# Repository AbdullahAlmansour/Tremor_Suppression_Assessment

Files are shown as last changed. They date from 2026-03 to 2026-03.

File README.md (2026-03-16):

# Tremor Suppression Assessment
This repository includes the instructions to build simple and affordable devices to test wrist exoskeletons for tremor suppression, which includes:
1 - a three-point bending machine to measure the stiffness,
2 - and an oscillatory wrist joint to simulate wrist tremor.
## 1 - Three Point Bending Device
This device was designs to assess the stiffness of a small exoskeleton. A linear displacement is applied on the exoskeleton by means of a servo motor and rack-and-pinion gearbox, and a load-cell is attached to the end effector to measure the applied force. 

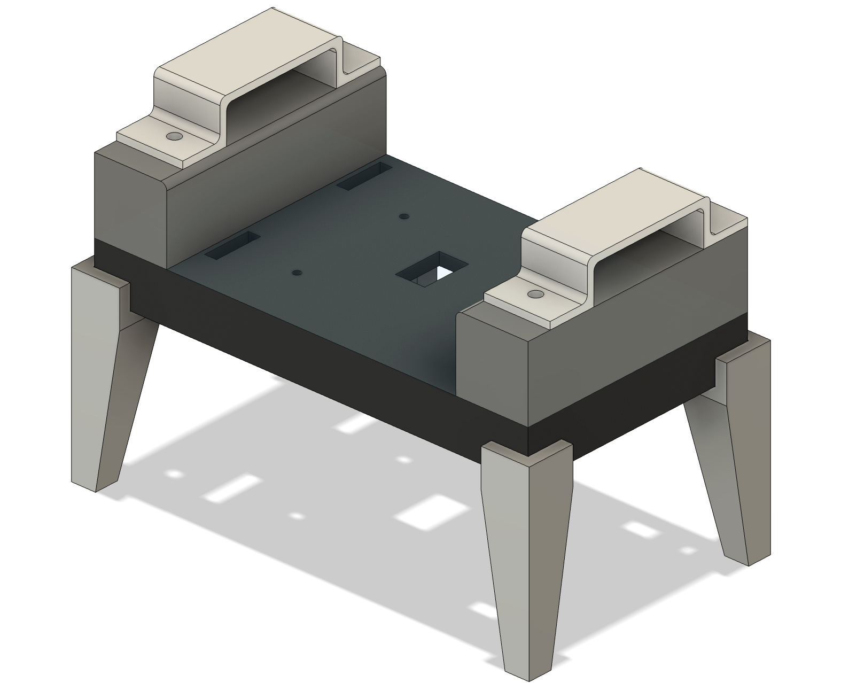
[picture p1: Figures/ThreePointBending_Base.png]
Base setup
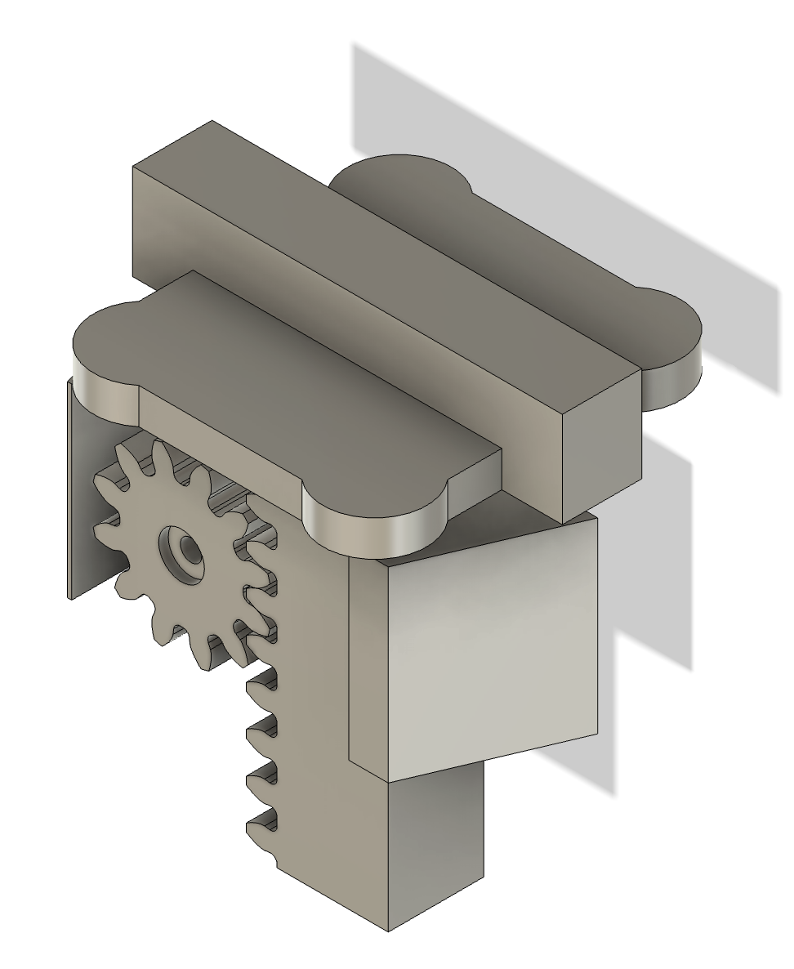
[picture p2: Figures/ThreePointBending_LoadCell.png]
Load cell setup
|  |  |
| :-----------------------------------------------: | :--------------------------------------------------------: |
|             **Figure 1:** Base setup              |               **Figure 2:** Load cell setup                |

The device consists of two main components:
- a base (Figure 1)
- an end effector (Figure 2)

The base was designed to securely hold the sample during testing and to mount the servo motor in the appropriate position. Its modular design allows stiffness measurements at different points of the exoskeleton. The end effector is actuated by an MG996R servo motor, where its angular displacement is converted into a linear displacement by means of a spur-to-linear gearbox. The tip of the end effector distributes the applied force equally onto four load cells encapsulated in a 3D-printed cap. These load cells are arranged in a Wheatstone bridge configuration, enabling precise measurement of small resistance changes, which are caused by mechanical deformation under load. 

The Wheatstone bridge converts resistance variations into a differential voltage signal in the millivolt range. To process this signal, the HX711 analog-to-digital converter (ADC) was used to amplify, filter, and digitise the output. The HX711 is a precision 24-bit ADC that is widely used in weighing scales and industrial control, designed specifically to interface with Wheatstone bridge sensors. It communicates with microcontrollers using a custom two-wire serial protocol (DT and SCK), accessible via the HX711\_ADC library. The HX711 continuously samples the signal and holds the converted data until clocked by the microcontroller, operating at a rate of $10~\mathrm{Hz}$.

### Tools and Components
- FDM 3D Printer (Flashforge 5M Adventurer was used)
- Caliber
- [MG996R Servo Motor](https://www.amazon.co.uk/Pzsmocn-Degrees-Helicopters-Robotic-Various/dp/B0CLGWKP3L/ref=sr_1_7?crid=2HTHPGAJ56Y6U&dib=eyJ2IjoiMSJ9.wogc4i2BFmTbbp_1KzUuA4kjO1IvbSnwEaeE4fUBs91m2Kxkljl7Gbayk552s1KByzJUdnbsghUo5_gd1sdZrULkUjtG6UXABx_IxFpicO-uQWcX5_VTm32dgz2BkLXvxuA14cW1wh0_4t-dmxXxa7OfmbNNnjPDXTDJ-t9xG873xbnqu7wY6JP6vZUN2P8INuiDiu57QHEsjP021zp0o9H9o6Igb4kDpZX3XIvhaG3LGmFQNnW7mmIch3pHO8D3ZLJ-1a-PGwNV_9ktzsRNQ9uoW8n37bhnylQkFCU67k8.gYzW6-Sh9fmm2UNK9i2hZv0QaoHroCeRyJPWE6vCacc&dib_tag=se&keywords=MG996R+Servo+Motor&qid=1773281587&sprefix=mg996r+servo+motor%2Caps%2C275&sr=8-7)
- [Four Strain-Gauge Sensors and HX711 Module](https://www.amazon.co.uk/YOUMILE-110lbs-Half-bridge-Weight-Resistance/dp/B07TWLP3X8)  

### Force Calibration

The HX711 ADC returns a unitless raw value $r$ that is proportional to the applied force $F$. Therefore, to determine the linear mapping parameters between the HX711 measurements and the applied force, a set of calibration masses in the range of $m \in [10,500]g$ were used. Assuming a gravitational acceleration of $g = 9.81~\mathrm{m/s^2}$, these masses correspond to an applied force of $F \in [0.0981,4.905] N$. The linear mapping is achieved by determining the parameters in linear equation
$$F = a + b \cdot r$$
where $F$ is the applied force in newtons, $r$ is the unit-less output from the HX711, and $a$, $b$ are the regression coefficients determined from the calibration data.

Given the calibration data vectors for applied force $\mathbf{F} = [F_1, F_2, \ldots, F_n]$ and corresponding raw sensor readings $\mathbf{r} = [r_1, r_2, \ldots, r_n]$, the linear model coefficient $\{a,b\}$ can be found using least squares method

$$
\boldsymbol{\theta} =
\begin{bmatrix}
a \\
b
\end{bmatrix}
= (\mathbf{X}^\top \mathbf{X})^{-1} \mathbf{X}^\top \mathbf{F},
\qquad
\mathbf{X} =
\begin{bmatrix}
1 & r_1 \\
1 & r_2 \\
\vdots & \vdots \\
1 & r_n
\end{bmatrix},
\qquad
\mathbf{F} =
\begin{bmatrix}
F_1 \\
F_2 \\
\vdots \\
F_n
\end{bmatrix}.
$$

where $\mathbf{X}$ is the $n \times 2$ matrix with a column of ones and a column of $r$ values, and $\mathbf{F}$ is the $n \times 1$ vector of measured forces. 

The calibration parameters $a$ and $b$ were found and used to fit the linear line, as shown in Figure 3.

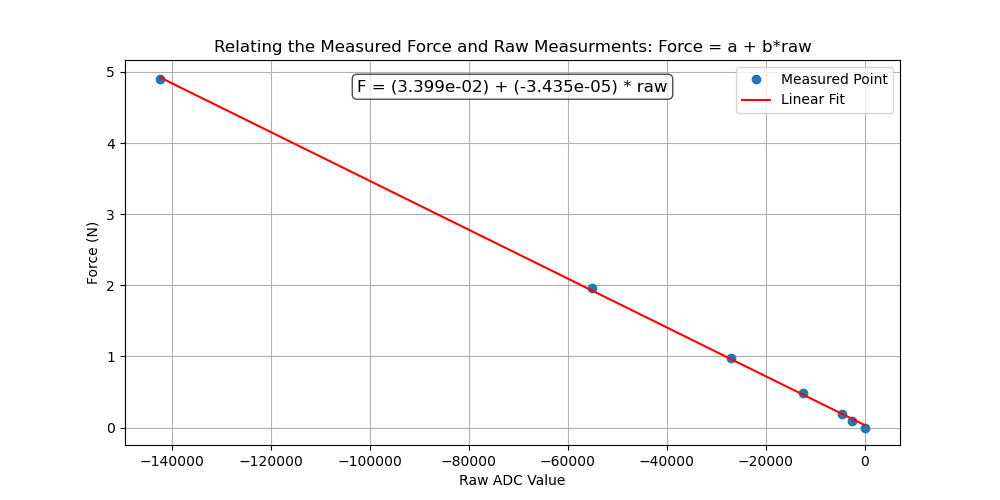
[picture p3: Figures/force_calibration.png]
ForceCalib
|                                                                                                       |
| :-----------------------------------------------------------------------------------------------------------------------------------------------: |
| **Figure 3:** Linear regression results for loadcell calibration, relating applied force (N) with the raw HX711 sensor output values (unit-less). |

### Displacement Mapping
The base servo motor receives its commands as pulse-widths $w$ in microseconds, controlled using the `ServoTimer2.h` library.  The corresponding servo rotation is converted to linear displacement through a spur-to-linear gear mechanism, shown in Figure 2.

To identify the relationship between the servo command $w$ and the resulting linear displacement $L$, the servo was actuated with commands in the range  $w \in [1000,2000] \mu s$ and a caliper was used to measure the corresponding loadcell displacement $L$.
A linear regression model is used to determine the mapping:

$$
L = c + d \cdot w
\tag{1}
$$

where \( L \) is the linear displacement in millimeters, \( w \) is the servo pulse-width command, and \( c \), \( d \) are the regression coefficients.

Given the calibration data vectors  
$\mathbf{L} = [L_1, L_2, \ldots, L_n]$ and  
$\mathbf{w} = [w_1, w_2, \ldots, w_n]$,  
the coefficients \(nc \) and \( d \) can be found using the least squares method:

$$
\mathbf{M}\,\boldsymbol{\delta} = \mathbf{L}, \qquad
\mathbf{M} =
\begin{bmatrix}
1 & w_1 \\
1 & w_2 \\
\vdots & \vdots \\
1 & w_n
\end{bmatrix}, \qquad
\boldsymbol{\delta} =
\begin{bmatrix}
c \\
d
\end{bmatrix}.
$$

The least–squares estimate is then given by:

$$
\boldsymbol{\delta}
= (\mathbf{M}^\top \mathbf{M})^{-1} \mathbf{M}^\top \mathbf{L}.
$$

The calibration parameters were found as $\mathbf{\delta} = [c, d]^T = [-0.0907, 0.01532]$, which achieved a good approximation of the linear mapping, as shown in Figure 4. A small sinusoidal error is observed, likely caused by the large teeth of the 3D-printed spur-to-linear gear. Using machined gears with finer teeth may improve the fit.

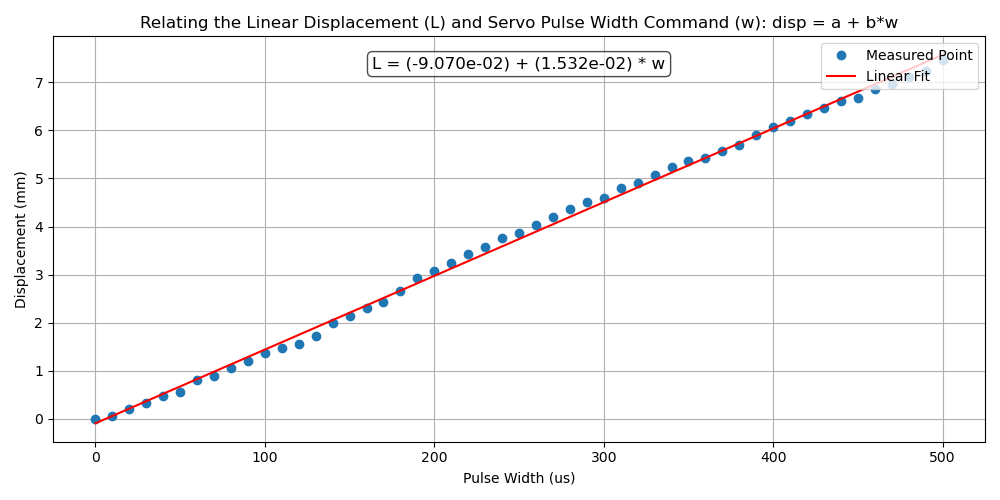
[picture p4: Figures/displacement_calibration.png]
|                                                                                                                |
| :--------------------------------------------------------------------------------------------------------------------------------------------------------------: |
| **Figure 4:** Linear regression results for loadcell calibration, relating the servo motor pulse width commands (us) with the measured linear displacement (mm). |

## 2 - Tremor Simulation Device
This device was designed to simulate wrist tremor oscillations in one direction (flexion/extension). The full setup is shown in Figure 5. The device consists of one joint and two links, which represent the wrist joint, hand link and forearm link, respectively. The two links are held onto the base using a low-friction metal rods to allow for free rotations. A third rod connects the two links with a potentiometer to measure the relative displacement between the links, and this constitutes the wrist revolute joint. 

The potentiometer wires are passed through a the hand link by a tunnel. A slot for for an IMU is also included as an alternative sensing method. The wrist oscillations are generated by a DC motor, that is attached to the joint through a damped crank-slider mechanism. The crank slider converts the DC motor's revolutions to continous linear oscillations, and the damper spring allows for applying adequate force without damaging the exoskeleton that is being tested. 

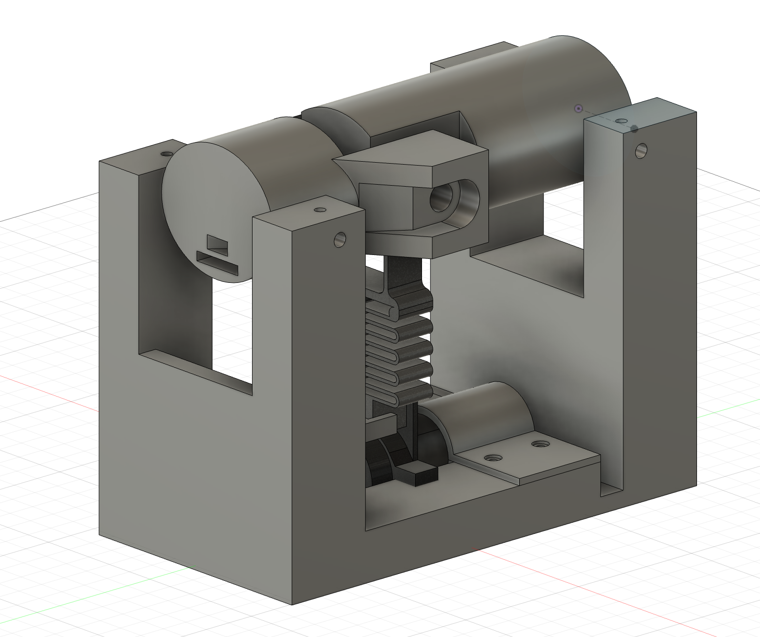
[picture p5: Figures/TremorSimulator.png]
|                                                                                                                |
| :--------------------------------------------------------------------------------------------------------------------------------------------------------------: |
| **Figure 5:** Tremor simulation device based on a damped crank-slider mechanism.|

### Tools and Components
- FDM 3D Printer (Flashforge 5M Adventurer was used)
- Caliber
- [DC motor with encoder](https://www.amazon.co.uk/Encoder-Gearbox-Reduction-Printers-Appliances/dp/B0GHFC8SPX/ref=sr_1_7?crid=3V12ZS7TYG7AQ&dib=eyJ2IjoiMSJ9.7ChXReGpV1Nz44734jPg72fY27dGEebMtGKmID6q4tHF-ybAWUQiLKophUnmO6xaE8Odwf85EIeip2Z2Ta07CcbffWimP2jFhUvrIJzVFroKgLPe6Z3v5fZHRm0GMMBSSwW3dRvMb7-RTptFflYydVa3BmaKu4NundIq42PIp3oWsfAitPF1EB3ug1SjrQTBXawe3bPCh8GcR_7z76fNwEkvn_7yYOsjCaHmWsqNFnxCAhSvb4T5rWJDTMY4pnCtUVQ3Rb9dH6Bkdi9t24qbHHK7UgELdkrw6lCOF0QgLp0.07acgIfQMGG2HAmeuMBrhvIYHRRICPvuZu-aOuTeLEI&dib_tag=se&keywords=Motor%2Bwith%2Bencoder%2B500%2BRPM&qid=1773527476&s=industrial&sprefix=motor%2Bwith%2Bencoder%2B500%2Brpm%2Cindustrial%2C290&sr=1-7&th=1) - choose motor with speed $\geq 180\,RPM$ after the reduction gearbox to simulate tremors of $\geq 3\,Hz$
- [Linear Potentiometer](https://www.amazon.co.uk/sourcing-map-Potentiometer-Single-Joint-JST-XH2-54/dp/B0F541XBYS/ref=sr_1_3_sspa?crid=GO473GHNYHN7&dib=eyJ2IjoiMSJ9.36QS7f7mTLfc2EXUiJEjk2_03l96p6q2KTj8MExBfrt02WOEm0LIkeNdiX64VXGGgYRrczsgifo2LjRuoeC3wWQJYy_-OwD9dHoF_MSdg6TM-cvQ6x8rdJ2f2vcY13mXaV-QA47BPjJkFTJzDsg7dKky8gG-0JVVLBcMUV2yZ0aix0ewW1kA79j7AbHd7fe0bHHaNVfoe_iwGyBlFCjkaFRmkLQ173ss9f4_ouIL7lcqeQ7j-48KqIjvxjXevH6I1Gh4BACCJdXhD8XEiFiYkoj-p_27R5DdVEg7QorXybc.whbxCKtb6a3vi67STffZVnArv6aEkiIXtedr5TvCa_E&dib_tag=se&keywords=Potentiometer%2Blinear&qid=1773593112&s=industrial&sprefix=potentiometer%2Blinear%2Cindustrial%2C296&sr=1-3-spons&aref=FcJdqy4bR3&sp_csd=d2lkZ2V0TmFtZT1zcF9hdGY&th=1)
- [IMU (MPU-6050)](https://www.amazon.co.uk/DollaTek-MPU-6050-mpu6050-Accelerometer-Arduino/dp/B07DJ4KMBF/ref=sr_1_4?crid=1WY24H8DKXBQK&dib=eyJ2IjoiMSJ9.AD3UVa4HQO0WjS3ZhZH_5vV_VdPCvc0ooA5QOkKDe39mLr0-LOH6r8rKYomtgEaCsg4i6xuScg7fCcr-su8IpTQxrYjvAbkZORndBr0_Fm8iJUvU31fKqIEtZDEMtBvV5T2zZ6xqSd44wllI03aIXcUB77-BE4n8vk2ZPHPIqS8CFGj-66HkgePCm4SkgQpDN-uNDxgtYWs_8H_Vk0qrsswj-GsLMnh4mWE5jXC96JbP72jfiI06Pf6RyfLGSnQKhUnO1KbB5456WHse8h77VcZoZ-VUw25vdOOLLR6Jldg.X0WeZ-Pe0cXJgKEocWoAWz1JN0zH_ntxPH_qgJSFrPI&dib_tag=se&keywords=IMU&qid=1773281448&sprefix=imu%2Caps%2C262&sr=8-4) - Optional

### Damped Crank Slider

The damped crank slider mechanism is shown in Figure 6. The crank slider converts the rotatory motion of the DC motor to linear oscillations, while the spring is used to damp the oscillations and allows for adequate force to be applied without damaging the exoskeleton. 

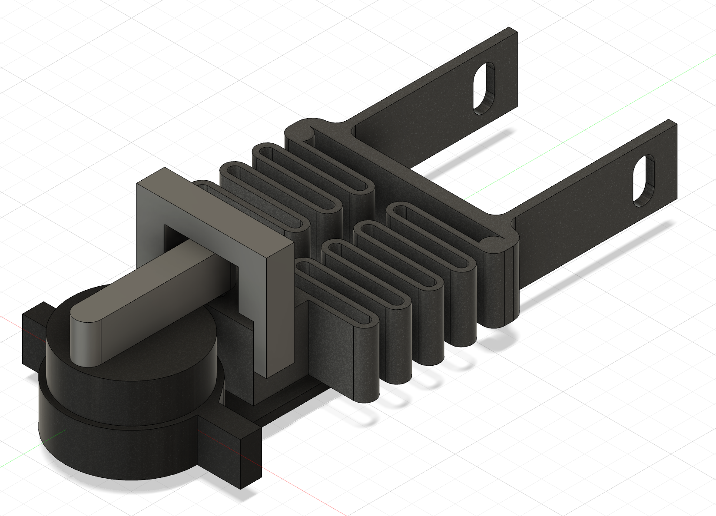
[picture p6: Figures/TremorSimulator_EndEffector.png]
|                                                                                                                |
| :--------------------------------------------------------------------------------------------------------------------------------------------------------------: |
| **Figure 6:** A DC-motor-driven damped crank-slider mechanism. |

#### Calibrating Spring Stiffness
To calibrate the spring stiffness to a value within the operating range of the variable stiffness exoskeleton, the spring stiffness must first be measured. 

The table in Figure 7 is used. The spring is attached between the base and the table suface, and some known calibration weights are places on the table surface. A caliber is used to measure the linear displacement of the spring, and the spring stiffness is found by calculating the gradient of the Force/Displacement graph.

$$
K = \frac{(F_2 - F_1)}{(x_2 - x_1)} = g\frac{(m_2 - m_1)}{(x_2 - x_1)}
$$

where $F_2$ and $F_1$ are two samples of linear force applied on the spring, which are equal to $g\,m_2$ and $g\,m_1$, respectively, while $x_2$ and $x_1$ are displacements corresponds to the applied linear forces. 

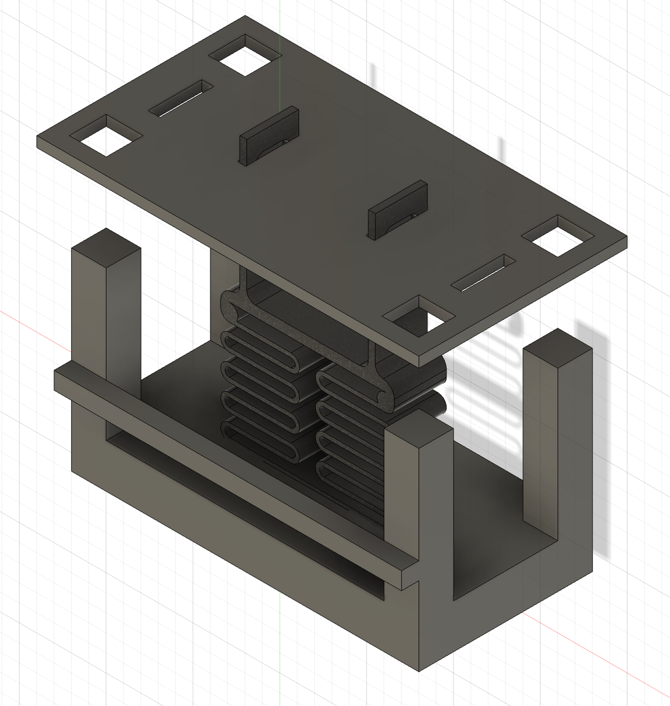
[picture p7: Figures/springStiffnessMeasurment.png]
|                                                                                                                |
| :--------------------------------------------------------------------------------------------------------------------------------------------------------------: |
| **Figure 7:** A stiffness measurement table. |

The spring stiffness can be increased to apply higher force by increasing the wire thickness, reducing its width, or reducing the number of loops. 

### Constant Oscillations
The encoder attached to the [DC motor](https://www.amazon.co.uk/Encoder-Gearbox-Reduction-Printers-Appliances/dp/B0GHFC8SPX/ref=sr_1_7?crid=3V12ZS7TYG7AQ&dib=eyJ2IjoiMSJ9.7ChXReGpV1Nz44734jPg72fY27dGEebMtGKmID6q4tHF-ybAWUQiLKophUnmO6xaE8Odwf85EIeip2Z2Ta07CcbffWimP2jFhUvrIJzVFroKgLPe6Z3v5fZHRm0GMMBSSwW3dRvMb7-RTptFflYydVa3BmaKu4NundIq42PIp3oWsfAitPF1EB3ug1SjrQTBXawe3bPCh8GcR_7z76fNwEkvn_7yYOsjCaHmWsqNFnxCAhSvb4T5rWJDTMY4pnCtUVQ3Rb9dH6Bkdi9t24qbHHK7UgELdkrw6lCOF0QgLp0.07acgIfQMGG2HAmeuMBrhvIYHRRICPvuZu-aOuTeLEI&dib_tag=se&keywords=Motor%2Bwith%2Bencoder%2B500%2BRPM&qid=1773527476&s=industrial&sprefix=motor%2Bwith%2Bencoder%2B500%2Brpm%2Cindustrial%2C290&sr=1-7&th=1) provides feedback in the form of pulses per revolution (PPR). In many cases, the supplier would provide this number in the datasheet, but for this particular supplier, the PPR was not included. Therefore, the [PPR Counter](Source%20codes/Arduino/PPRCounter) arduino code was provided to count the PPR by manually rotating the motor shaft for one revolution and taking note of the number via the Terminal. Alternatively, you can use an oscilloscope to determine this.

Using the speed feedback, a PI controller can be applied to maintain constant oscillations at the desired frequency, by measured the error

$$
e_k = S_{d} - S_{m_k}
$$

where $S_{d}$ is the desired speed in RPM and $S_{m_k}$ is the measured speed at the current time sample using the encodor. The integration of error is performed in discrete time as:

$$
e_{I_{k}} = e_{I_{k-1}} +  e_k \Delta{t}
$$

where $e_{I_{k}}$ is the integral of error at the current time sample, $e_{I_{k-1}}$ is the integral of error at the previous time sample, and $\Delta{t}$ is the sampling time period.

The PI control law is then:
$$
u_{pwm} = k_p\, e_k + k_I\,e_{I_{k}} 
$$
where $k_p$ and $k_I$ are the proportional and integral gains, respectively. The arduino code to implement the PI controller is provided in [Constant Oscillations](Source%20codes/Arduino/constantOscillations).

### Oscillations FFT
The the gyroscrope measurements from [IMU (MPU-6050)](https://www.amazon.co.uk/DollaTek-MPU-6050-mpu6050-Accelerometer-Arduino/dp/B07DJ4KMBF/ref=sr_1_4?crid=1WY24H8DKXBQK&dib=eyJ2IjoiMSJ9.AD3UVa4HQO0WjS3ZhZH_5vV_VdPCvc0ooA5QOkKDe39mLr0-LOH6r8rKYomtgEaCsg4i6xuScg7fCcr-su8IpTQxrYjvAbkZORndBr0_Fm8iJUvU31fKqIEtZDEMtBvV5T2zZ6xqSd44wllI03aIXcUB77-BE4n8vk2ZPHPIqS8CFGj-66HkgePCm4SkgQpDN-uNDxgtYWs_8H_Vk0qrsswj-GsLMnh4mWE5jXC96JbP72jfiI06Pf6RyfLGSnQKhUnO1KbB5456WHse8h77VcZoZ-VUw25vdOOLLR6Jldg.X0WeZ-Pe0cXJgKEocWoAWz1JN0zH_ntxPH_qgJSFrPI&dib_tag=se&keywords=IMU&qid=1773281448&sprefix=imu%2Caps%2C262&sr=8-4) in the Y axis, the FFT of oscillations was plotted, while maintaining the frequency at $3\, Hz$. The dominant frequency is observed at approximately $3\,Hz$, as well as its harmonics at $6\,Hz$

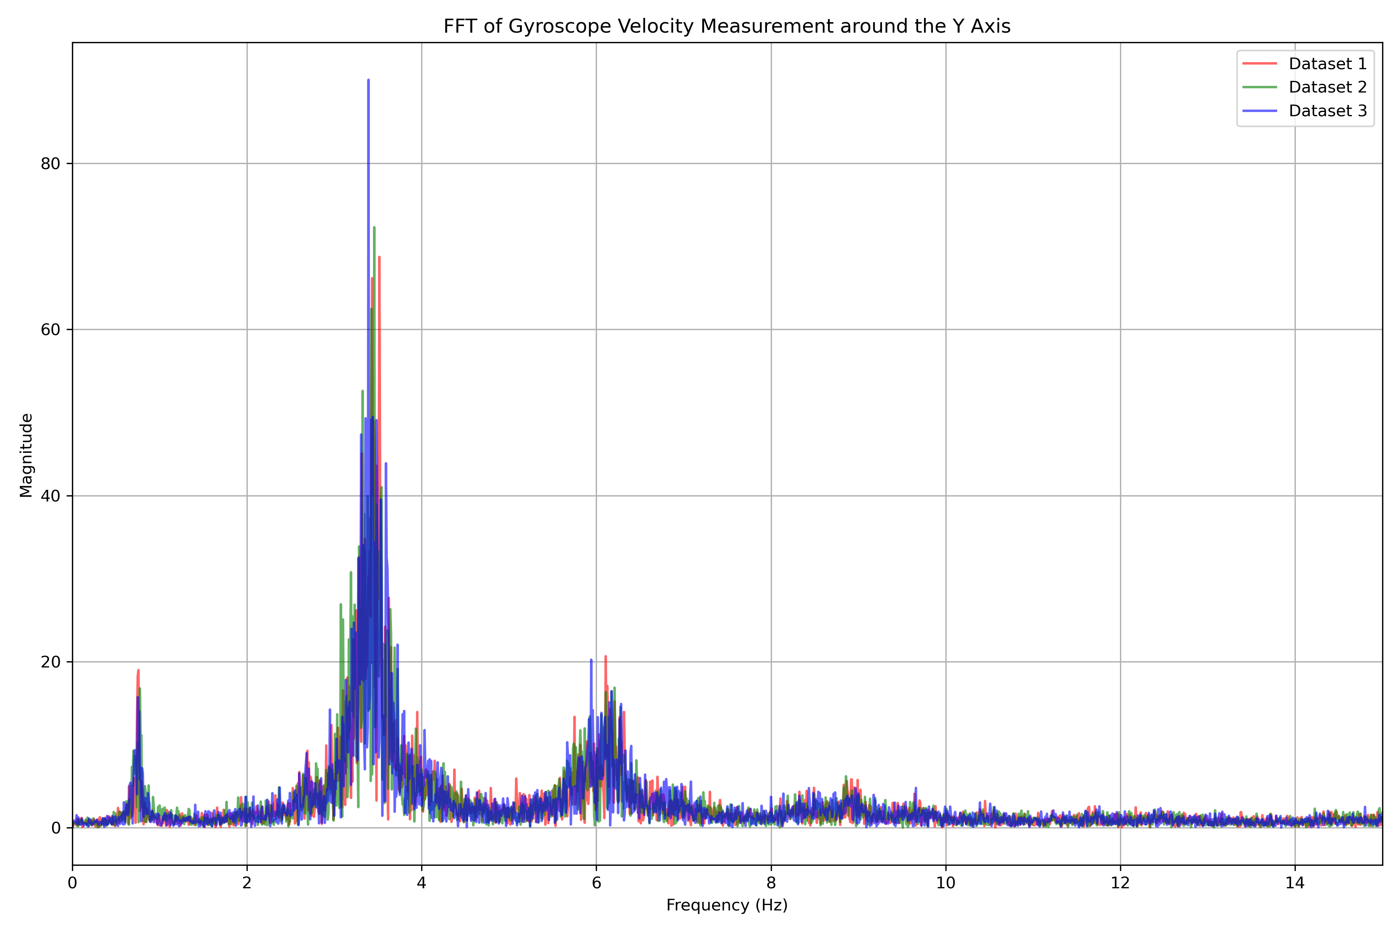
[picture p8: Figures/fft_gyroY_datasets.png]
|                                                                                                                |
| :--------------------------------------------------------------------------------------------------------------------------------------------------------------: |
| **Figure 8:** FFT of the tremor simulation device, obtained from the gyroscope measurements |

### Conclusion
This repository provides two economic methods to assess soft wrist exoskeleton with variable stiffness. The first method (three-point bending machine) can be used to measure the stiffness of a small exoskeleton device, while for more precise measurements or for stiffer materials, you may need to consider an industrial option such as [Instron's three-point bending machine](https://www.instron.com/en/products/testing-accessories/flexure-fixtures/three-point-bend-test-fixtures/). The second method assess the dynamic response of the wrist exoskeleton by applying constant oscillatory movement, and two means to measure change in angular oscillations, either by an IMU or a potentiometer. These two methods can be used to verify the validity of the variable stiffness exoskeleton.

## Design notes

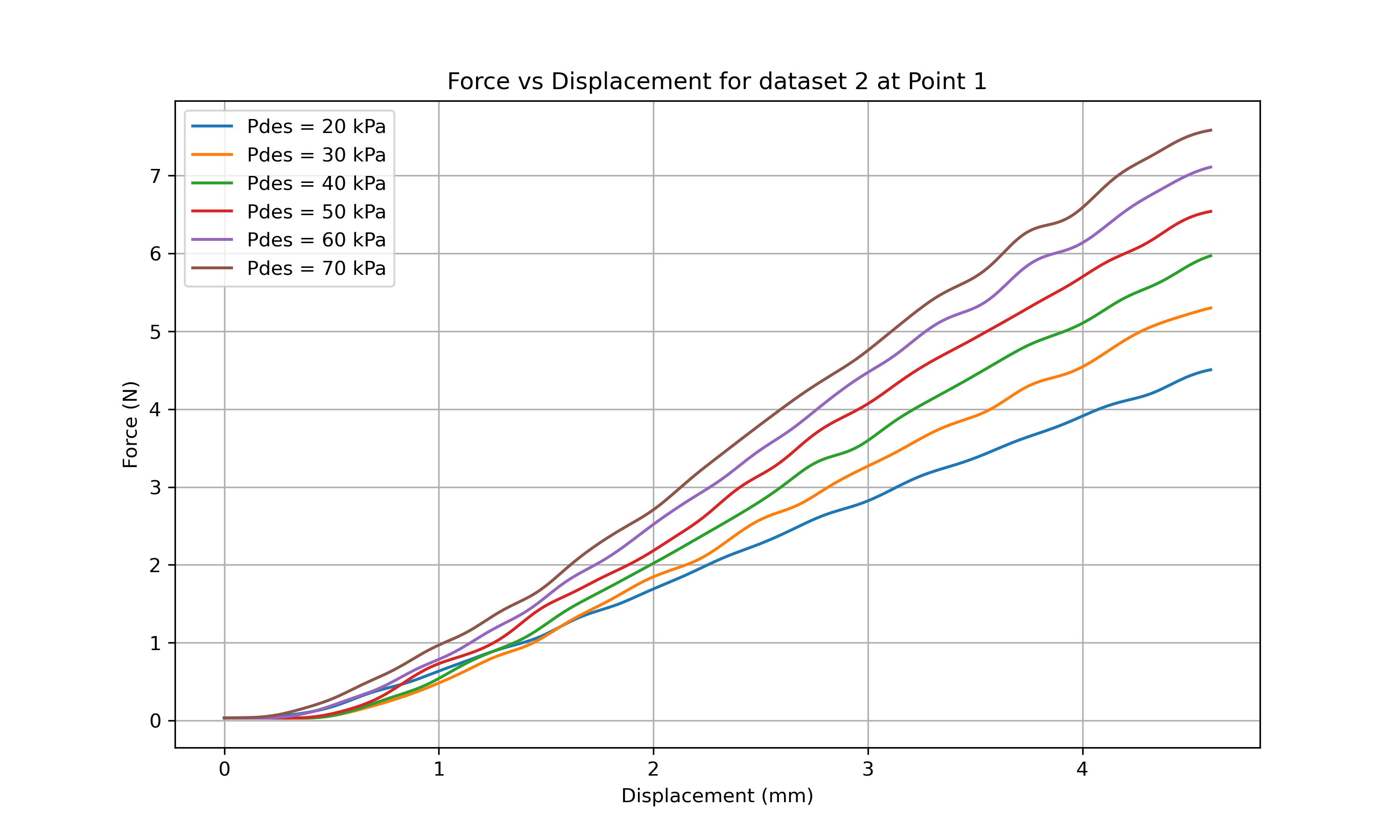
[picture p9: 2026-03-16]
Figures/figure_3.png

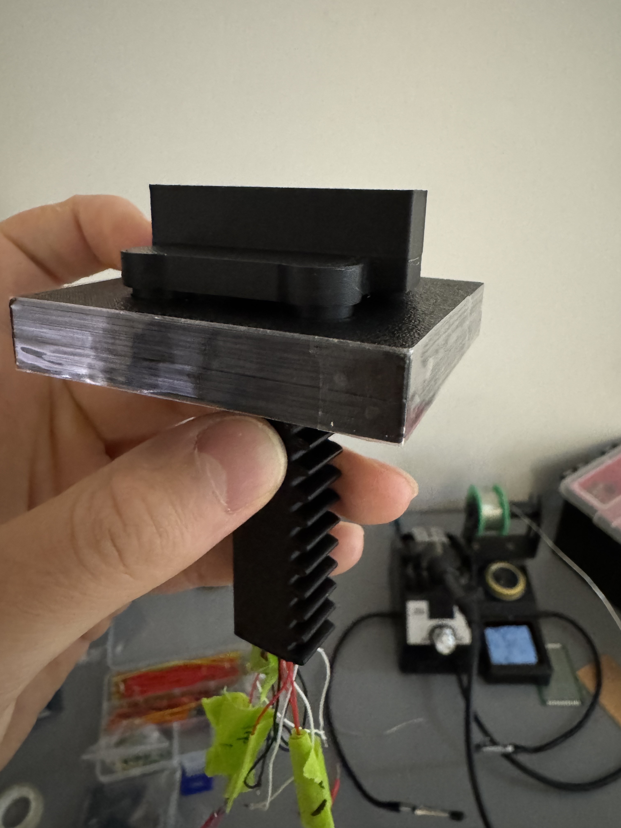
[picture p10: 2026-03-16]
Figures/force2.jpg

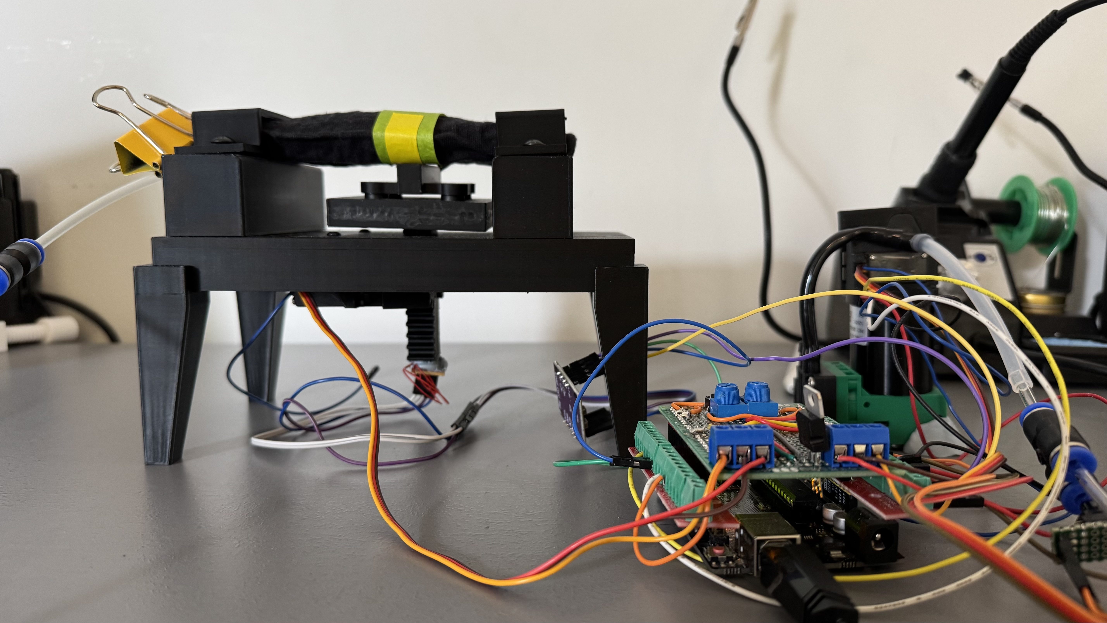
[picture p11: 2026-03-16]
Figures/point1.jpg

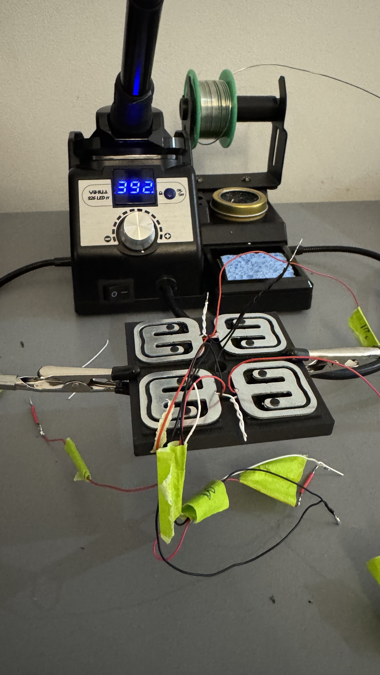
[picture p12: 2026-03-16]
Figures/force3.jpg

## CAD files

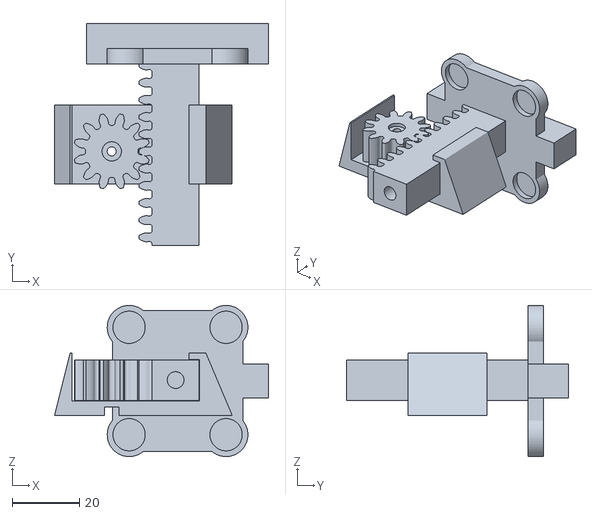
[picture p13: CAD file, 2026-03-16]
3D Printing Files/ThreePointBendingMachine/loadcellGears.stl
63.6 x 66.0 x 44.9

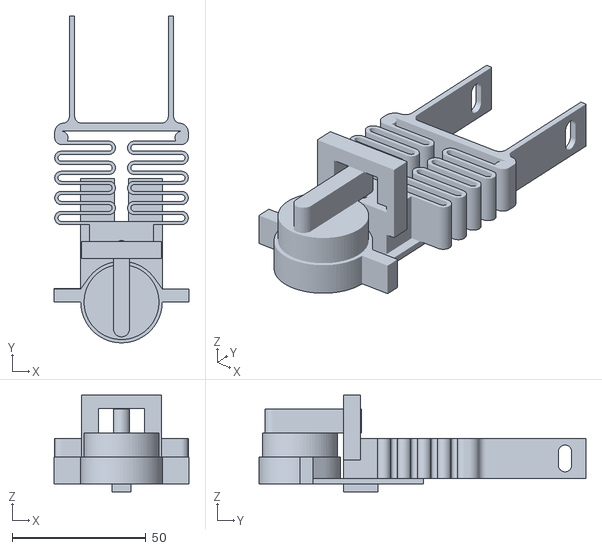
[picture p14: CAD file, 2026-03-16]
3D Printing Files/TremorSimulator/dampedCrankSlider.stl
50.5 x 122.2 x 36.2

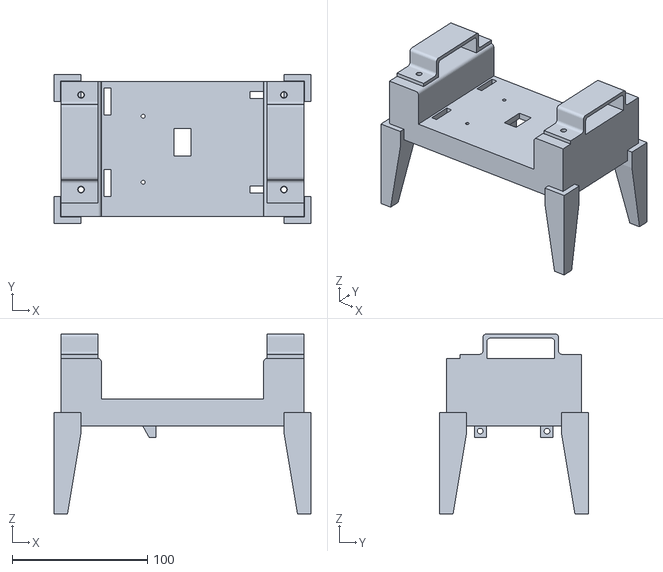
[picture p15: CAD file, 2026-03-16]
3D Printing Files/ThreePointBendingMachine/ForceExperiment.stl
190.0 x 110.0 x 133.0

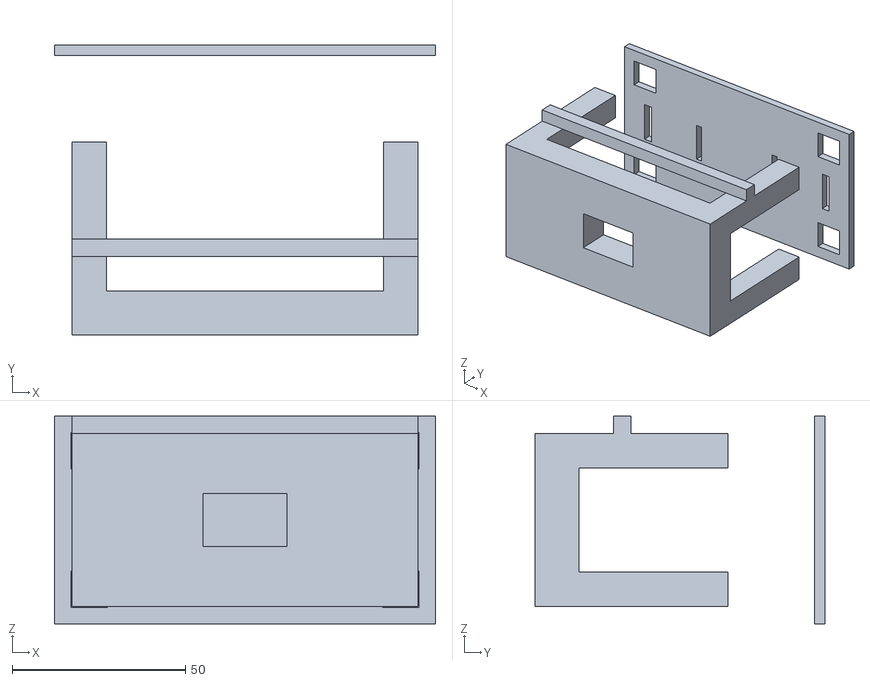
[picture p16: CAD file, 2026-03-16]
3D Printing Files/TremorSimulator/springStiffnessMeasurementTable.stl
110.0 x 83.7 x 60.0

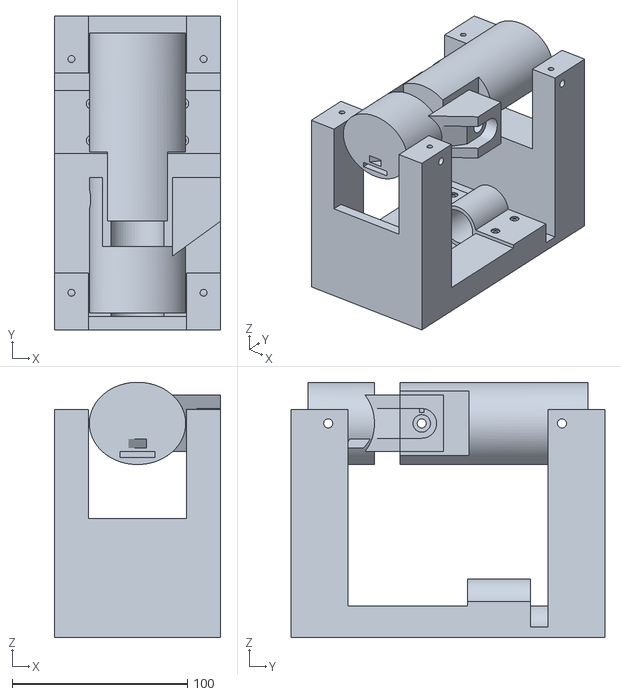
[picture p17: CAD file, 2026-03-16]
3D Printing Files/TremorSimulator/TremorSimulator_Base.stl
95.0 x 179.4 x 145.9

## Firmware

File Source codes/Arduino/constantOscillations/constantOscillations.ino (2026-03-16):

// Pin definitions
#define ENC_A 2 // Yellow wire from encoder
#define ENC_B 3 // Green wire from encoder (not used)
#define PPR 200 // Pulses Per Revolution (depends on the encoder)
#define ENA_motor 6 // PWM pin for motor speed control

// Global variables
volatile long pulseCount = 0; // Interrupt Service Routine (ISR) for the encoder

float motorRPM = 0;
float f_des = 3; // Desired frequency in Hz 
float rpm_des = f_des * 60.0; // Desired speed in RPM
float motor_duty = 0; 

// PI control variables
float e = 0.0;
float e_acc = 0.0;
float kp = 20.0;
float ki = 2.0;

// Timer variables for speed calculation
unsigned long prevMillis = 0; // Timer for speed calculation
unsigned long t_prev = 0.0;
float t_diff = 0.0;


void setup() {
  // Set encoder pins with pull-up resistors
  pinMode(ENC_A, INPUT_PULLUP);
  pinMode(ENC_B, INPUT_PULLUP);
  // Set motor control pin as output
  pinMode(ENA_motor, OUTPUT);
  // Attach interrupt to the encoder A channel
  attachInterrupt(digitalPinToInterrupt(ENC_A), encoderISR, CHANGE);

  Serial.begin(115200); // Start serial communication
  t_prev = millis(); // Initalise the timer
}

void loop() {
  unsigned long t_now = millis();
  t_diff = (float)(t_now - t_prev);
  
  // Update speed every 20ms
  if (t_diff >= 20) {
    // Calculate motor speed in RPM
    noInterrupts();
    long count = pulseCount;
    pulseCount = 0;
    interrupts();
    motorRPM = ((float)count / (float)PPR) * 60.0 * (1000.0 / t_diff);

    // PI control
    e = (rpm_des - motorRPM); // Calculate error in speed
    
    e_acc += e * (t_diff / 1000.0); // Accumulate error over time (integral term)
    motor_duty = kp * e + ki * e_acc; // PI control law to calculate motor duty cycle

    // Clamp duty [0, 255]
    if (motor_duty < 0) motor_duty = 0;
    if (motor_duty > 255) motor_duty = 255;

    // Set motor speed
    analogWrite(ENA_motor, (int)motor_duty);
    t_prev = t_now; // Update timer for next speed calculation
  }
}

void encoderISR() {
  pulseCount++;
}
